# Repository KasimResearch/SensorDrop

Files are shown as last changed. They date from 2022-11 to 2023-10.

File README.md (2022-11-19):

# SensorDrop

SensorDrop is an open-source system for remotely detaching individual animal-borne sensors from wildlife collars.

SensorDrop builds upon and extends the functionality of existing open-source full wildlife collar detachment mechanisms [1], and is the result of over 800 hours of additional development and field-testing time. 

# Repository structure

The SensorDrop repository is organised around design and schematics files needed for the development of SensorDrop units:

- For producing: contains all of the needed design files, schematics, and parts lists to independently manufacture SensorDrop units. 
- Supplemental information: contains information to help with key SensorDrop design choice considerations (e.g., potential pitfalls and lessons learnt in user deployments)

# Further information

A more detailed overview of SensorDrop and its use in wildlife science will be covered within a manuscript (currently under peer-review). 

A link to the manuscript will be provided upon its publication.

[1] Rafiq, K., Appleby, R. G., Edgar, J. P., Jordan, N. R., Dexter, C. E., Jones, D. N., Blacker, A. R. F., & Cochrane, M. (2019). OpenDropOff: An open-source, low-cost drop-off unit for animal-borne devices. Methods in Ecology and Evolution, 10(9), 1517–1522. https://doi.org/10.1111/2041-210X.13231

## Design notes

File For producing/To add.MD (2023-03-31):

## To Add
- Add pictures to the instructions to make it easier
- Add instructions on the simplest way to create the nylon webbing holes

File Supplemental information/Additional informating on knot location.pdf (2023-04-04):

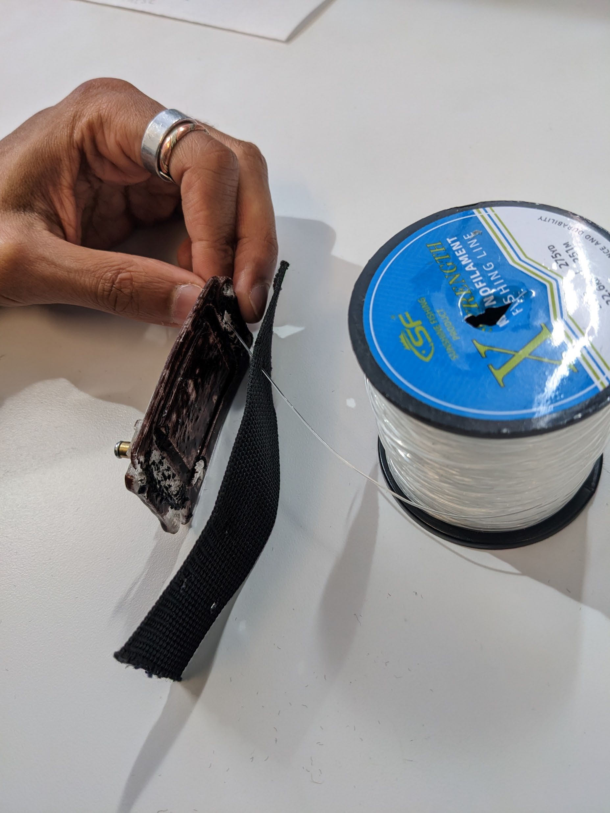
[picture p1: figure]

Step 1.

Thread the nylon through one of the five belting holes and the mirroring drop-off plate hole.

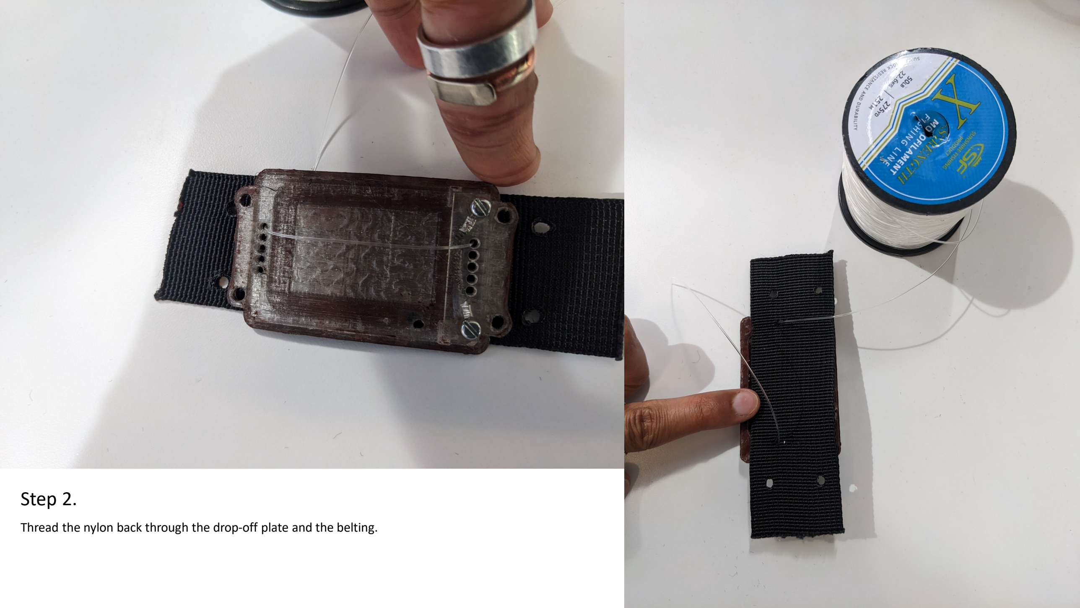
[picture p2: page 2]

Step 2.

Thread the nylon back through the drop-off plate and the belting.

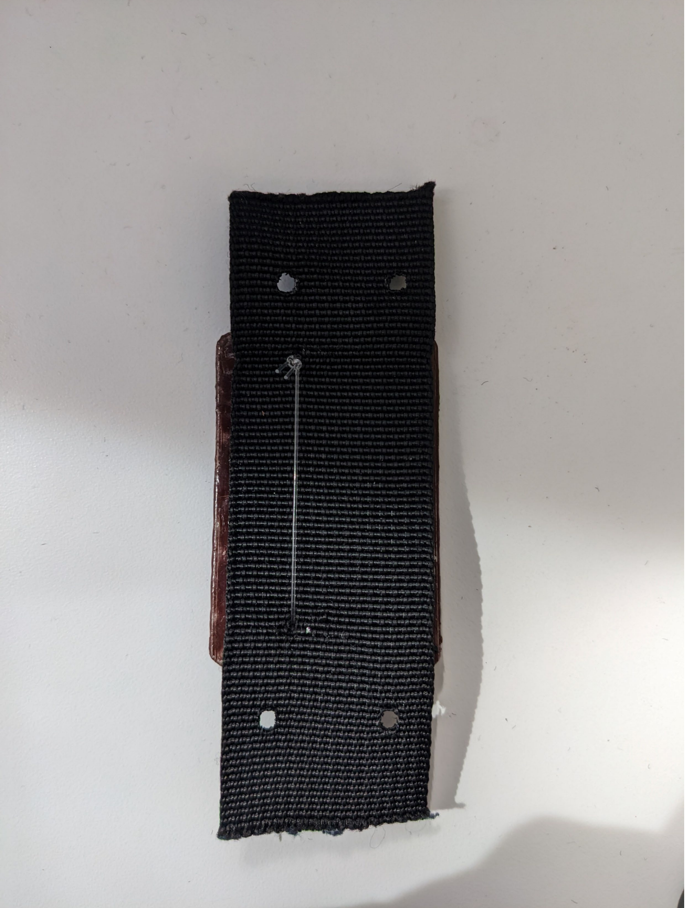
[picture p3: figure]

Step 3.

Tie a knot
In previous deployments, we used the Weston knot: https://youtu.be/s_CJI2GZFdQ

Repeat steps 1-3 for as many of the four other holes (not shown in image) as needed.

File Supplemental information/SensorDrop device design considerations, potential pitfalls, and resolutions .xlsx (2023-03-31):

Issue | Possible cause | Possible solutions
Open flame on nichrome | Too much current is passing into the nichrome element and the temperature it reaches is causing an open flame | - Increase the length of nichrome element used. - Increase the wire length between the battery and OpenDrop PCB and/or the nichrome element and the OpenDrop PCB. - Use a larger guage (thicker) of nichrome. - Use a lower-capacity battery
Water ingress through drop-off plate holes | Holes in the drop-off plate needing to be sealed | - Fill the drop-off plate holes with silicon sealant and allow it to cure completely. Then coat your nylon line with a silicon based lubricant before threading it through the silicon sealed holes.
Nylon line knot failing | - Unsuitable knot used - Too thick of a nylon line used | - Try using a weston knot (see https://youtu.be/s_CJI2GZFdQ) - Once the knot is tied, place a small drop of super glue onto it and allow it to dry.
Nichrome element breaking upon heating | Too much current is passing into the nichrome element and is causing the nichrome to weaken and snap. | - Increase the length of nichrome element used. - Increase the wire length between the battery and OpenDrop PCB and/or the nichrome element and the OpenDrop PCB. - Use a larger guage (thicker) of nichrome. - Use a lower-capacity battery
VHF transmitter not used meaning there is a hole in the bottom of the drop-off plate. | NA | Fill the hole with silicon sealant and allow it to cure completely. This will technically be a 'weak' point in the drop-off plate. However, the location of this point, i.e., against the belting, means it will face significant exposure to the environment once the SensorDrop system detaches.

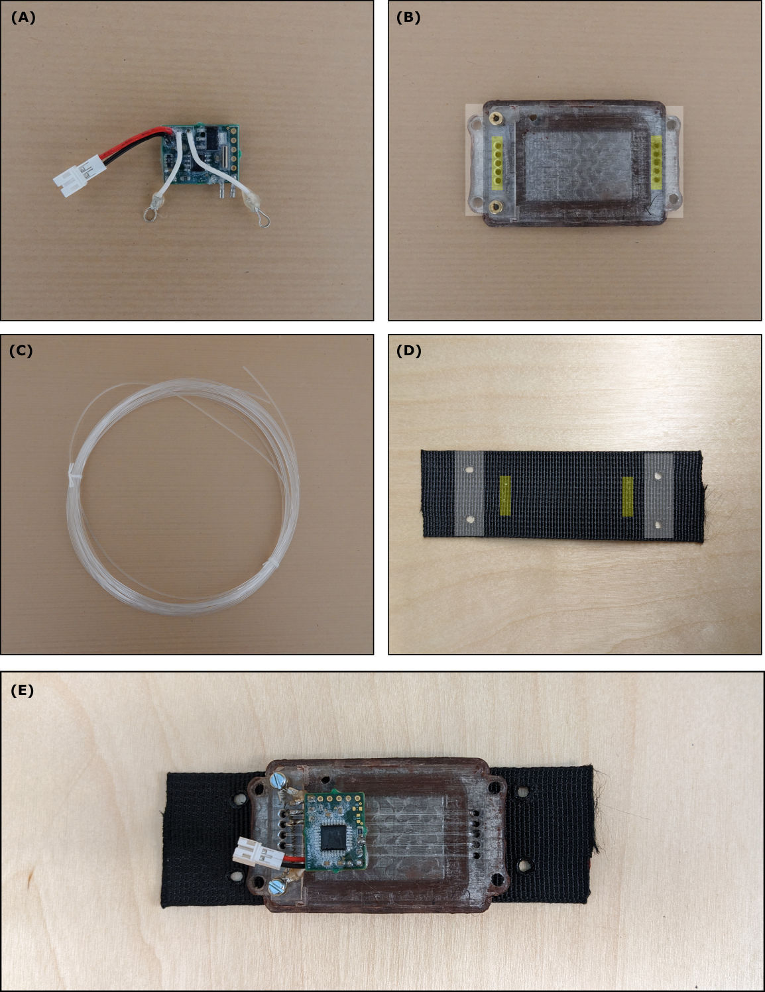
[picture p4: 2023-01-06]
Images/Figure 1.png

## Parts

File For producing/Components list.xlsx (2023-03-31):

Component | Qty | Supplier Part Number | Price per SensorDrop (USD) | Minimum order price (USD) | Material specifications △ | Website
OpenDrop PCB
PCB | 1 | NA | $10.66 | $ 10.66 (enough for 1 SensorDrop) |  | Self-producible (see Rafiq et al., 2019)
Wires (power and nichrome) | 2 | C2003W-5-ND | $0.14 | $ 0.99 (enough for 7 SensorDrops) | Cable type: hook-up; gauge: 24 AWG; conductor strand: solid; conductor material: copper, annealed tinned | www.digikey.com
Ring terminals | 4 | 795-1677 | $0.39 | $ 9.72 (enough for 25 SensorDrops) | Inner ring diamater: 3.68 mm; outer ring diamater; 6.35; contact material: copper; contact plating: tin | www.rs-online.com
Battery (Turnigy 200 mAH ) | 1 | 9067000498 | $3.49 | $ 3.49 (enough for 1 SensorDrop) | Battery type: lithium polymer; capacity: 200 mAh; voltage 3.7V; constant discharge rate: 20C | www.hobbyking.com
Drop-off plate
3D printed plate | 1 | NA | $6.76 | $ 6.76 (enough for 1 SensorDrop) | Printing material: Polylactic Acid (PLA) | www.3dpeople.uk/
Acrylic plate | 1 | B09DP33SP8 | $0.28 | $ 13.99 (enough for 50 SensorDrops) | 2 mm thick acrylic (plexiglass) | www.amazon.com
Brass spacer | 2 | 1772-2606-ND | $2.52 | $ 2.52 (enough for 1 SensorDrop) | Material: brass; thread size: M2.5x0.45 | www.digikey.com
Nichrome wire | 1 | B07CHTT73J | $0.02 | $ 7.39 (enough for 300 SensorDrops) | Single strand nichrome; gauge: 28 | www.amazon.com
Spacer screw | 2 | 36-29300-ND | $0.96 | $0.96 (enough for 1 SensorDrop) | Type: machine screw; material: steel; plating: zinc, clear chromate; thread size: M2.5x0.45 | www.digikey.com
Nylon line
Nylon line | 1 | B0928JDY9Y | $0.03 | $ 7.99 (enough for 250 SensorDrops) | Monofilament fishing nylon, uncoated, and 50 lb (22.6 kg) tensile strength. | www.amazon.com
Nylon webbing
Nylon webbing | 1 | WN250-BLACK | $0.11 | $ 0.89 (enough for 8 SensorDrops) | Weave nylon webbing | www.profabrics.co.uk
Total SensorDrop price |  |  | $ 25.36 *
* Since some SensorDrop materials must be purchased in packages with more materials than required for a single SensorDrop unit (see minimum order price), the initial material costs for a single SensorDrop unit are $60.77, with costs further reducing to the $25.36 unit cost as more units are developed.
△ We provide material specifications for users who want or need to purchase alternative parts than those suggested. Part recommendations are based on component specifications during African wild dog deployments. Other materials/specifications may also be suitable. In all cases, we recommend thorough testing within a controlled environment before deploying on animals.

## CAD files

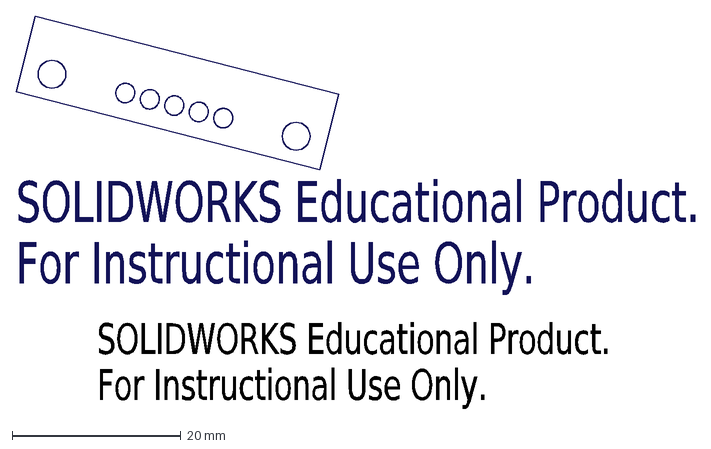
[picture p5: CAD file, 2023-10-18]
For producing/2021_07_19_acrylic_plate.DXF
SOLIDWORKS Educational Product.
For Instructional Use Only.

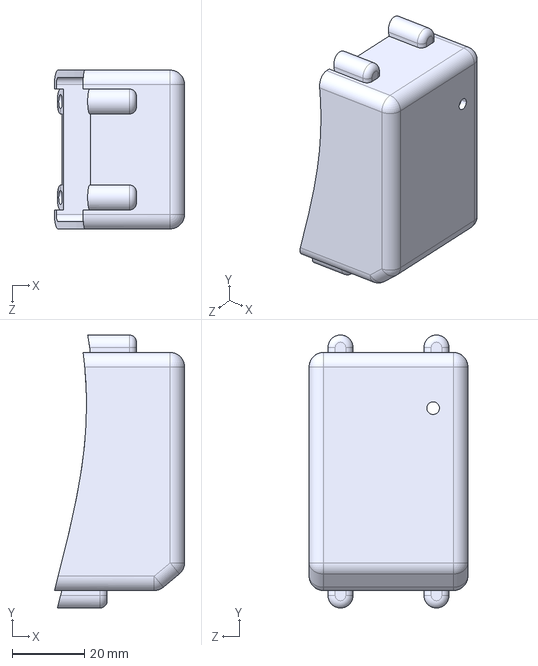
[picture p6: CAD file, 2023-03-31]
For producing/SensorDrop_wildDog enclosures.STEP
36.1 x 75.7 x 44.0 mm

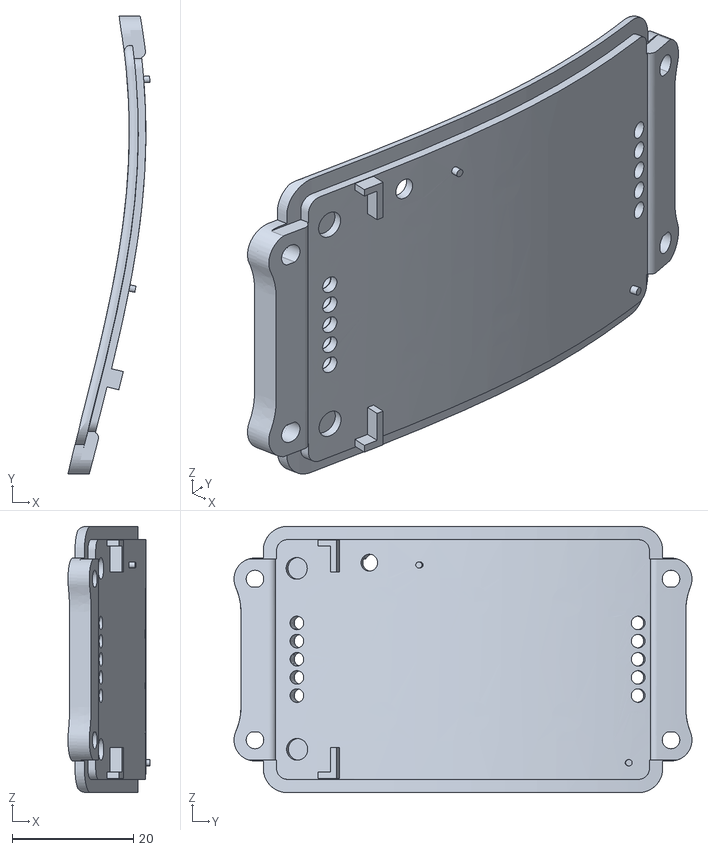
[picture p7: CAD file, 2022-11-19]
For producing/SensorDrop_drop off plate.STL
13.6 x 75.7 x 44.0

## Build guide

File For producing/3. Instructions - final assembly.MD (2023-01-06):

## Components needed
- Assembled drop-off plate x 1
- Assembled nichrome element x 1
- Assembled OpenDrop PCB x 1
- Nylon webbing with holes matching the drop-off plate x 1
- Brass spacer screws x 2
- Nylon line x 1 roll

## Additional items needed
- Scissors
- Pliers 
- Silicone lubricant (optional)
- Super glue (optional)
- Thread locker (optional)

## Instructions 

1. Screw the nichrome element onto the brass spacers using the crimped loops. 
2. Place the drop-off plate onto the nylon webbing – lining up the holes. 
3. Thread the nylon line through one nylon webbing hole and the associated hole on the drop-off plate's underside. Run the nylon line across the top of the plate lengthways, over the nichrome element, and back through the drop-off plate and nylon webbing. Once you have done this, you’ll need to tie the ends together to maintain the tension on the line. If the line is loose, there is poor contact with the nichrome element, so the line won’t be melted through when the nichrome element heats. The best knot I’ve found for this is the Weston Knot (typically used for surgery: see here for a demonstration on how to tie, https://www.youtube.com/watch?v=s_CJI2GZFdQ)
Please note that if you have previously sealed your drop-off plate holes with silicon sealant, you must do two additional things. First, you’ll need to cut the leading end of the nylon line (the one that goes through the holes) at an angle, so it’s pointy enough to poke through the silicon. Second, you’ll need a silicon-based lubricant to coat the nylon line before poking it through the silicon. This second step means there’s enough slippage for the nylon line to flow through the holes when the line is severed. 
4. Repeat this for all five lines (or as many lines as you want).
5. Once you have all five lines (or as many as you want) tied, you can optionally add a small drop of super glue to the knot itself. This adds an extra layer of protection against the knot coming undone. However, be careful that no super glue gets between the drop-off plate and the nylon webbing, as this will prevent the plate from detaching. 
6. Unscrew the brass spacer screws. Attach the OpenDrop PCB to the system by threading the brass spacer screws through the OpenDrop wire loop and the nichrome element loop, then screw it all tightly to the brass spacer. If you’re worried about the screws coming undone with vibration, add a drop of thread locker glue to the screw as an extra safety step. 
7. You now have a finished drop-off plate with a drop-off mechanism. Your final steps would be to (i) set the drop-off system date ([see here](https://doi.org/10.1111/2041-210X.13231) and the associated [GitHub repository](https://github.com/Wild-Spy/OpenDrop)), (ii) screw your user-designed housing for the sensors onto the drop-off plate, and (iii) bolt or rivet the nylon webbing onto the wildlife collar. 

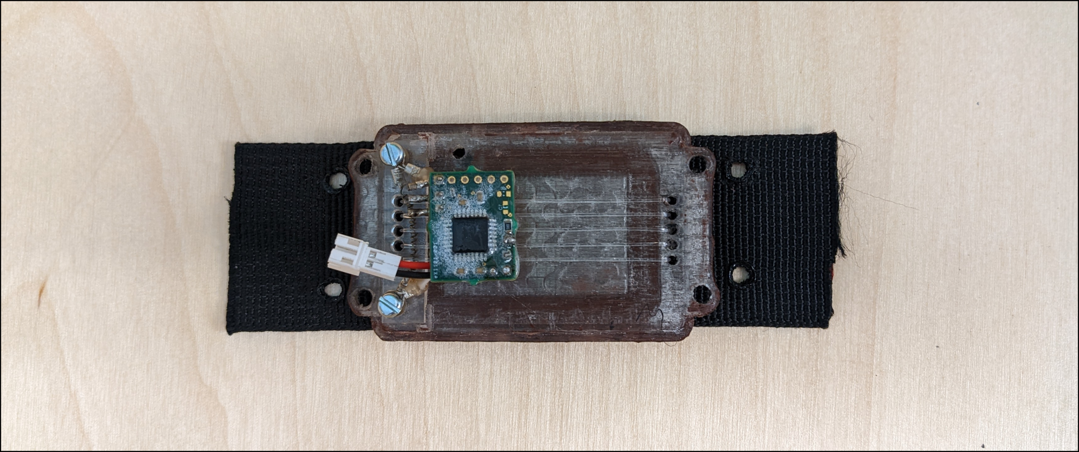
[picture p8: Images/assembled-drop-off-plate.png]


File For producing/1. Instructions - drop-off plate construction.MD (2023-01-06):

## Components needed
- 3D printed plate x 1
- Acrylic plate x 1
- Brass spacer x 2

## Additional items needed
- Superglue
- Soldering iron
- Flat head screwdriver 
- Silicon sealant (optional)

## Instructions 
1. Using a small amount of superglue, glue the acrylic plate onto the end of the drop-off plate with the two holes carved to accommodate the brass spacer. To help line up the holes on the acrylic plate with the holes on the drop-off plate, two walls have been added to the drop-off plate. Placing the acrylic plate flush against these walls creates alignment with everything. Note that when you add the glue, ensure it does not contact the five holes where the nylon line will go through. 
2. Once the super glue has dried. Place a brass spacer in one of the two larger holes created for it. It won’t go fully into the space created for it, but that’s okay. Once the spacer is in the hole, heat your soldering iron. Carefully apply the soldering iron tip to the top of the brass spacer and gently press down. Be careful, as this will heat the brass spacer. As the brass spacer heats, it will slowly melt into the cavity created for it. Once the lip of the bottom of the brass spacer is level with the acrylic plate, remove the soldering iron. Apply a tiny amount of super glue to where the brass spacer and the acrylic plate meet so that the adhesive can seep into the cavity. Allow it to dry, and repeat the above steps with the other brass spacer.
3. OPTIONAL: if you want to waterproof the holes where the nylon line passes through, you can use silicon sealant (e.g., Technicqll Black High-Temperature Silicone Adhesive Sealant). To do this, flip the drop-off plate upside down and fill each of the holes with silicon sealant. A thin layer here is fine. You don’t want to fill it so much that the sealant goes entirely through to the other side of the plate. Allow it to dry for at least 48 hours (or however long the manufacturer recommends). 

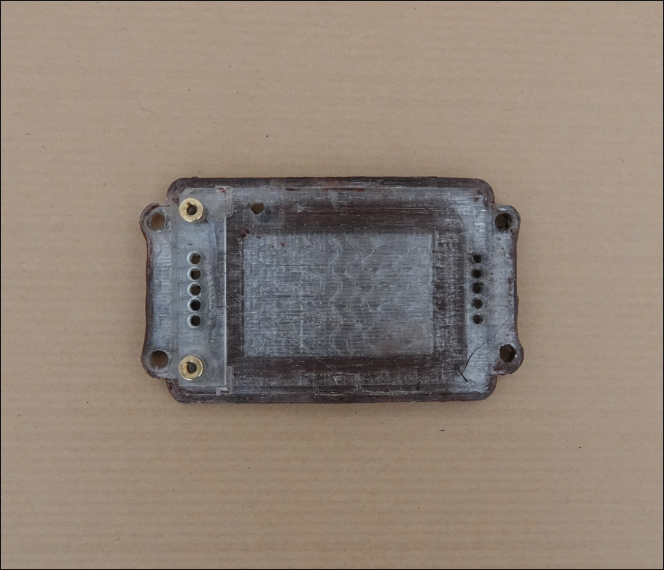
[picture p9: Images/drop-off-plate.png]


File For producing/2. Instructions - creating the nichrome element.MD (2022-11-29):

## Components needed
- Nichrome wire x 1 roll
- Ring terminals x 2
- Brass spacer screw x 1

## Additional items needed
- Sewing Pin x 1
- Wire cutters
- Pliers 
- Callipers 

## Instructions for constructing the same nichrome element as the wild dog case study
1. Cut 90 mm of 28AWG nichrome element. 
2. Use wire cutters to cut the end of the ring terminal off so that all you have remaining is the crimping section. 
3. Wrap one end of the nichrome element around the screw, leaving only enough space at the wrapped end that would accommodate the length of the crimping section you created from the previous step.
4. Slide the created crimp onto the nichrome element and crimp closed the loop you have just created. Slide out the screw. 
5. Repeat steps 2-4 for the other end of the nichrome element. 
6. The crimped loops on each end should have taken around 17.5 mm of nichrome element to create. This means that you should have approximately 55 mm of straight nichrome from the end of one crimp to the end of the other crimp. Check if this is true using callipers. Any divergence could lead to the nichrome heating to higher temperatures (leading to an open flame) or not reaching high enough temperatures to melt the nylon line. Before deploying, you should pre-test your finished nichrome element in a controlled environment.
7.  Once you are happy that the space between the crimps is 55 mm (or whatever other length you choose), you need to coil the nichrome. To create consistent and tight coils, you will coil the nichrome element around the sewing pin. Starting at one end of the nichrome element, use the pliers to grasp the other end of the nichrome element and coil it tightly around the sewing pin. You want to have the coils as close together as possible. Once finished, slide the sewing pin out. 
8. Take the coiled nichrome element and gently stretch it to the appropriate width using the nichrome plate brass spacers to measure how long it should be. When stretching the nichrome element, you want to (a) keep the coils as consistently spaced as possible and (b) make sure that none of the coils are touching each other.

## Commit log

2022-11-29 Create 3. Instructions - final assembly.MD
2023-01-06 Update 3. Instructions - final assembly.MD
2023-03-31 Add files via upload
    Updated components list
    [Components list.xlsx]
2023-10-18 Added the nichrome plate file
    [2021_07_19_nichrome_plate.DXF]
2024-04-24 Update and rename 2021_07_19_nichrome_plate.DXF to 2021_07_19_acrylic_plate.DXF
    Amended the name to match the documentation
    [2021_07_19_acrylic_plate.DXF]
2024-04-24 Delete For producing/SensorDrop_acrylic plate.stl
    Deleted broken file
    [SensorDrop_acrylic plate.stl]
